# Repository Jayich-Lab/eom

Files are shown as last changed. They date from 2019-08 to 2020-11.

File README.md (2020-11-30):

# Electro-optic Modulator

The design for this project is based heavily on work done in the [Will Lab](https://www.will-lab.com/) that they generously shared with us.

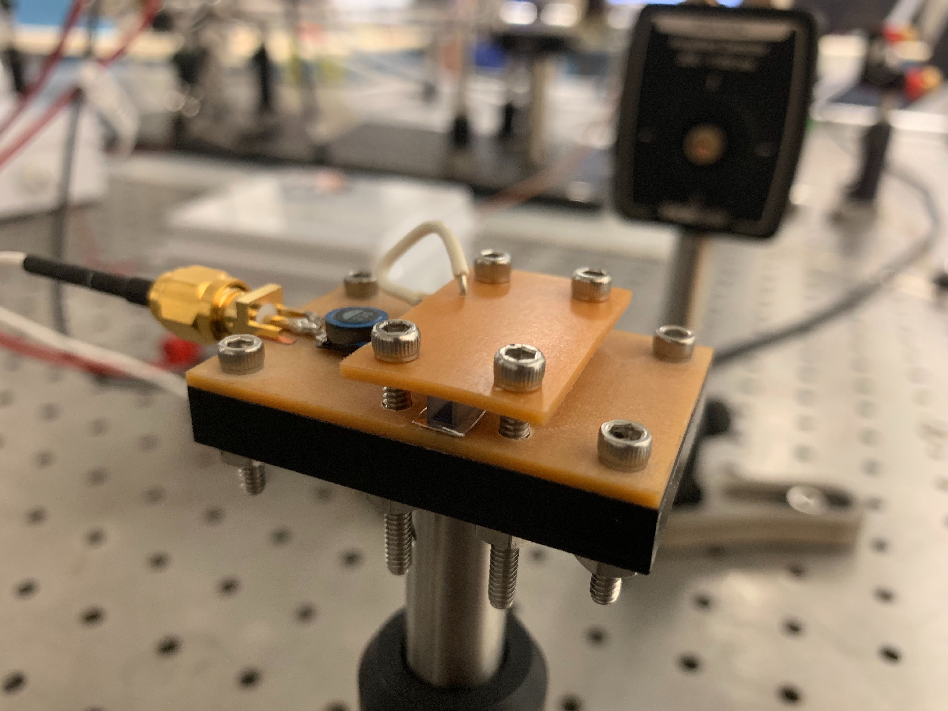
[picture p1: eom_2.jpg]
eom2


## EO Crystal 

We chose Lithium niobate (LiNbO<sub>3</sub>). It has a good Pockels effect, so we can minimize the input voltage to achieve the required modulation depth.
#### Relationship between the index of refraction, the electro-optic tensor, and the electric field:

<div align="center">\begin{pmatrix} \Delta(\frac{1}{n^{2}})_{1}\\ \Delta(\frac{1}{n^{2}})_{2}\\ \Delta(\frac{1}{n^{2}})_{3}\\ \Delta(\frac{1}{n^{2}})_{4}\\ \Delta(\frac{1}{n^{2}})_{5}\\ \Delta(\frac{1}{n^{2}})_{6} \end{pmatrix}= \begin{pmatrix} r_{11} &r_{12} &r_{13} \\ r_{21} &r_{22} &r_{23} \\ r_{31} &r_{32} &r_{33}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</div>

#### Electro-optic tensor of LiNbO<sub>3</sub> -- 3m(C3v) point group:
<div align="center">\bar{\bar{r}}=\begin{pmatrix} 0&-r_{22} &r_{13} \\ 0&r_{22} &r_{13} \\ 0&0 &r_{33} \\ 0&r_{42} &0 \\ r_{42}&0 &0 \\ -r_{22}&0 &0 \end{pmatrix} </div>  

#### Electro-optic Coefficient for Lithium Niobate (LiNbO<sub>3</sub>):

Electro-optic Coefficient | Value (pm/V) | 
:---: | :---: | 
r<sub>13</sub> | 9.6 
r<sub>22</sub> | 6.8
r<sub>33</sub> | 30.9 
r<sub>42</sub> | 32.6  

Taken from Boyd, 2003. This is within a [margin of error](http://www.lambdaphoto.co.uk/pdfs/Inrad_datasheet_LNB.pdf).

## Required voltage for changing a π phase

The "cut" of a crystal is the direction light is meant to propogate through it, e.g. Y-Cut means light will travel in the Y direction of crystal (where the X, Y, Z directions are specified by the crystal geometry). The voltage required for a pi phase shift is determined by the cut.

Applied electric field in Z direction, wave propagates in Y direction (Y-Cut):

<div align="center">V_{\pi}=\frac{d\lambda}{L(r_{33}n_{e}^{3}-r_{13}n_{o}^{3})}</div>  

<br/><br/>

Applied electric field in Y direction, wave propagates in Z direction (Z-Cut):
<div align="center">V_{\pi }=\frac{d\lambda }{4Ln_{0}^{3}r_{22}}</div>

#### Refractive Index for Lithium Niobate (LiNbO<sub>3</sub>) at different wavelengths

Value for n<sub>e</sub> | Value for n<sub>o</sub>  | Laser wavelength 
:---: | :---: | :---:
2.2666 | 2.3650 | 468nm
2.2342 | 2.3232 | 532nm
2.1875 | 2.2715 | 708nm
2.1845 | 2.2680 | 728nm
2.1702 | 2.2491 | 852nm
2.156 | 2.232 | 1064nm

---

## Final Design

We used Y-cut lithium niobate as our EO crystal. The bandwidth needed was 400nm-1100nm. We used different AR coatings to cover this range, one from 400-700nm and one from 700-1100nm. The crystal is 3mm x 3mm x 30mm, where one face is 3mm x 3mm.

#### The voltage needed across the EO crystal is:

λ( in meter ) | V<sub>π</sub> ( in volts )
:---: | :---: 
468 × 10<sup>-9</sup> | 201 V
532 × 10<sup>-9</sup> | 237 V
708 × 10<sup>-9</sup> | 335.65 V
852 × 10<sup>-9</sup> | 412 V
1064 × 10<sup>-9</sup> | 524.325 V

---

## Resonant circuit
We used a resonant circuit to minimize the input voltage which keeps the device safe to operate and avoids the extra effort of generating that high voltage.

The resonant frequency can be calculated:



We can use the usual parallel plate capacitor formula to calculate capacitance: 
<div align="center">C=\epsilon _{33}\frac{A}{d}</div>

Permittivity for Lithium Niobate is a tensor:
<div align="center">\begin{pmatrix} \epsilon_{11} &0 & 0 \\ 0 &\epsilon_{11} &0 \\ 0 &0 &\epsilon_{33} \end{pmatrix}</div>

If we apply electric field in Z direction, we are going to use ε<sub>33</sub>

Parameter | Value | Description
:---: | :---: | :---: 
ε<sub>33</sub> | 0.2543 × 10<sup>-9</sup> | permittivity for lithium niobate (in F⋅m<sup>−1</sup>) (about 28~30 times larger than ε<sub>0</sub>)
A | 0.003 × 0.03 | area of two plates (in meters<sup>2</sup>)
d | 0.003 | distance between plates (in meters)
C | 7.629 × 10<sup>-12</sup> | Capacitance of the crystal 

We use impedance to calculate the V<sub>eom</sub> with respect to input voltage (V<sub>eom</sub> is the voltage difference of two plates between the EO crystal). V<sub>input</sub> is the applied voltage before the resonant circuit. R<sub>sma</sub> is the resistance of SMA RF connector. R<sub>load</sub> is the resistance for the circuit.

<div align="center">V_{eom}=\frac{X_{C}}{X_{C}+X_{L}+R_{sma}+R_{load}}V_{input}</div>

<div align="center">\left |V _{eom} \right |=\frac{1}{\omega _{0}(R_{sma}+R_{load})C_{eom}}V_{input}</div>

R<sub>sma</sub> = R<sub>load</sub> = 50 Ω  

C = 7.629 × 10<sup>-12</sup> (approximately)

We need a modulation frequency f = 10 MHz = 10<sup>7</sup> Hz so we need L ~ 33.2uH

Quality factor for this circuit (RLC circuit) Q ~ 20

So the the maximum voltage required to operate is ~25 V.

There will obviously be stray capacitance and other non-ideal effects. In practice our quality factor was about 6, and our resonant frequency was ~8.7MHz.

---

Parts used:

- [ ] [33.2uH inductor chip](https://www.digikey.com/product-detail/en/tdk-corporation/SLF7032T-330MR75-2PF/445-2005-1-ND/755412)
- [ ] [RF Connector (50ohm)](https://www.digikey.com/products/en?keywords=SMA-J-P-H-ST-EM1)
- [ ] (2) Indium foil (~4mm x 30mm)
- [ ] Lithium Niobate crystal
- [ ] [Delrin stock (to be milled, <13mm thickness is ideal)](https://www.mcmaster.com/plastics/wear-resistant-easy-to-machine-delrin-acetal-resin-sheets-bars-and-strips/thickness~1-2/)
- [ ] (8) 4-40 screws
- [ ] (8) 4-40 nuts
- [ ] (1) 8/32 screw
- [ ] [(4) Spring Washers](https://www.mcmaster.com/spring-washers/curved-disc-springs-6/id~0-135/)
- [ ] 8/32 compatible 1/2" optics post
- [ ] 1/2" optics post holder

---

# Instructions on how to build the EOM

First, mill the mount (generally any plastic works, but delrin was used for our EOMs). The mount design is in the repo as a fusion360 model and an stl/step model. 

Second, mill the top and bottom pcbs. Set a large clearance (20 mm) when milling them such that all copper visible on the board is for required lines. The eo crystal will be sandwiched in between the top and bottom pcbs, with the indium foil as a cushion. You should then solder the inductor and the sma connector onto the bottom pcb. It is advisable to solder the top pcb to the bottom for the ground connection at this point (leaving a reasonable amount of slack on the wire used).

You then want to take the eo crystal and gently place that between ~4mmx30mm strips of indium foil between the pcbs. (Make sure the side of the eo crystal used is correct!) Finally, screw everything together -- first screw the mount onto the 1/2" post, then the bottom pcb onto the mount, then the top pcb onto the mount (through the bottom pcb). Note that we use 4-40 screws with spring washers to do so.

You should be careful not to break the eo crystal when tightening. We found that not much force is required to make electrical contact. Note that our resonant frequency on the circuit was 8.7MHz, but you could change this by changing the inductance (were you in need of a different modulation frequency).

N.B. Try to make sure the screws are tightened somewhat evenly. Uneven pressures on the crystal are most likely to break it (fixed by spring washers).

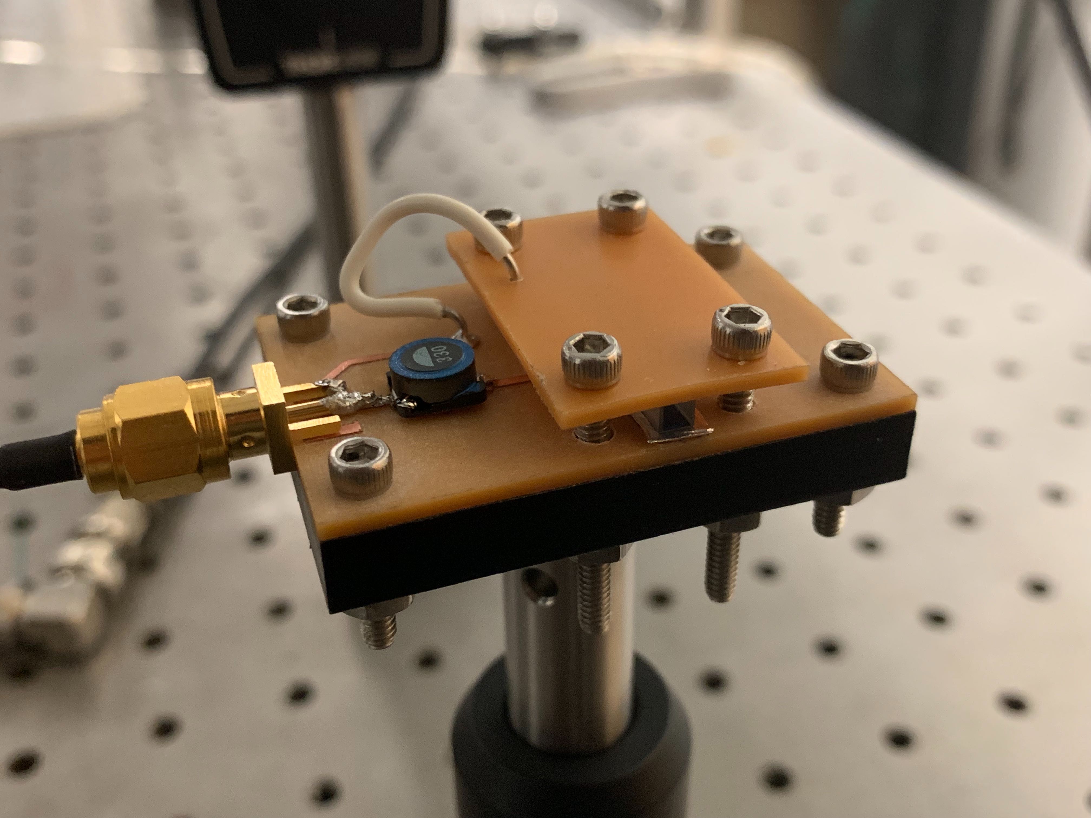
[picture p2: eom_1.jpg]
eom1


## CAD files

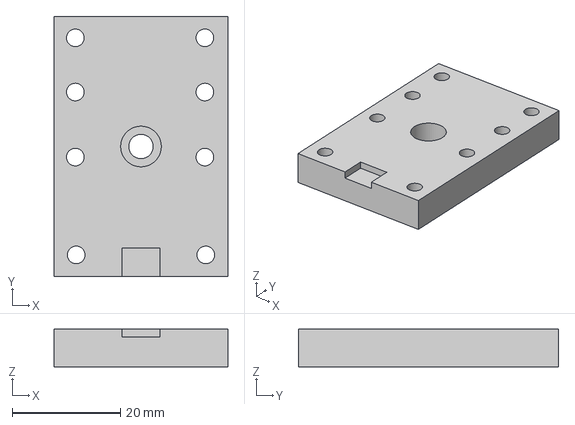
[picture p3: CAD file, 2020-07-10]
design/plastic mount/EOM_pcb_adapter v6.step
32.1 x 48.0 x 7.00 mm

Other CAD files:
design/plastic mount/EOM_pcb_adapter v6.f3d
design/plastic mount/EOM_pcb_adapter v6.stl

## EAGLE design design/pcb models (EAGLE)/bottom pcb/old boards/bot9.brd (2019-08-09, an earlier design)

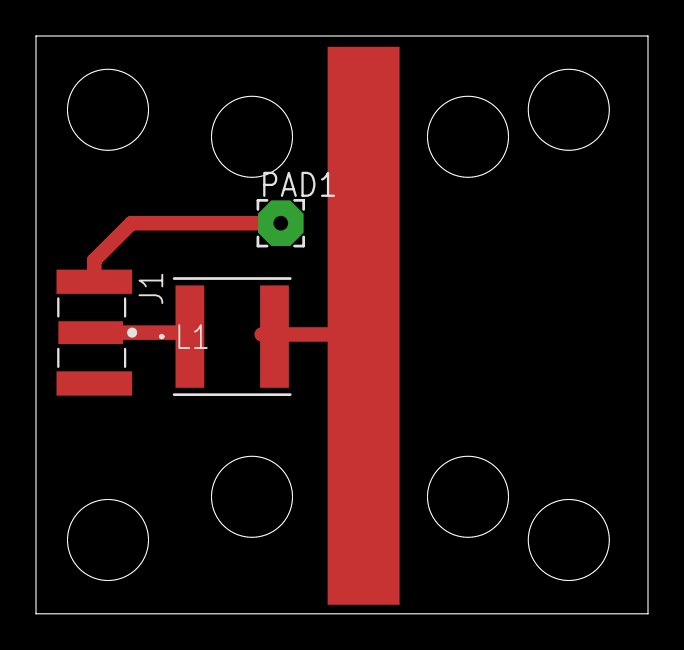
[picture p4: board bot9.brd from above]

Board: 2 copper layers, 34.0 x 32.1 mm, 3 parts (0 on the bottom side), 2 nets.

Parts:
J1: SMA-J-P-H-ST-EM1
L1: NR6028T330M; IND_TAIYO_NR6028
PAD1: 2,54/0,8

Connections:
unnamed: J1.1, L1.2
unnamed: J1.2_1, J1.2_2, J1.3_1, J1.3_2, PAD1.1

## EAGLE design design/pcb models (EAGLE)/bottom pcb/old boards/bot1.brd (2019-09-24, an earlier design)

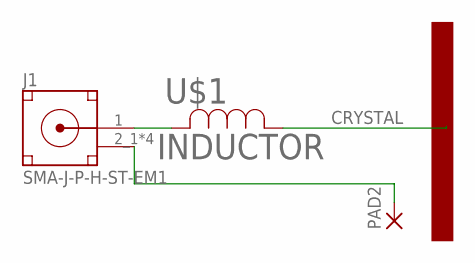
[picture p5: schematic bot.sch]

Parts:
J1: SMA-J-P-H-ST-EM1
PAD2: 2,54/1,1
U$1: INDUCTOR; IND_7030

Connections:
2L: J1.1 (SIGNAL), U$1.2
CRYSTAL: U$1.1
GND: J1.2_1 (GND), J1.2_2 (GND), J1.3_1 (GND), J1.3_2 (GND), PAD2.1

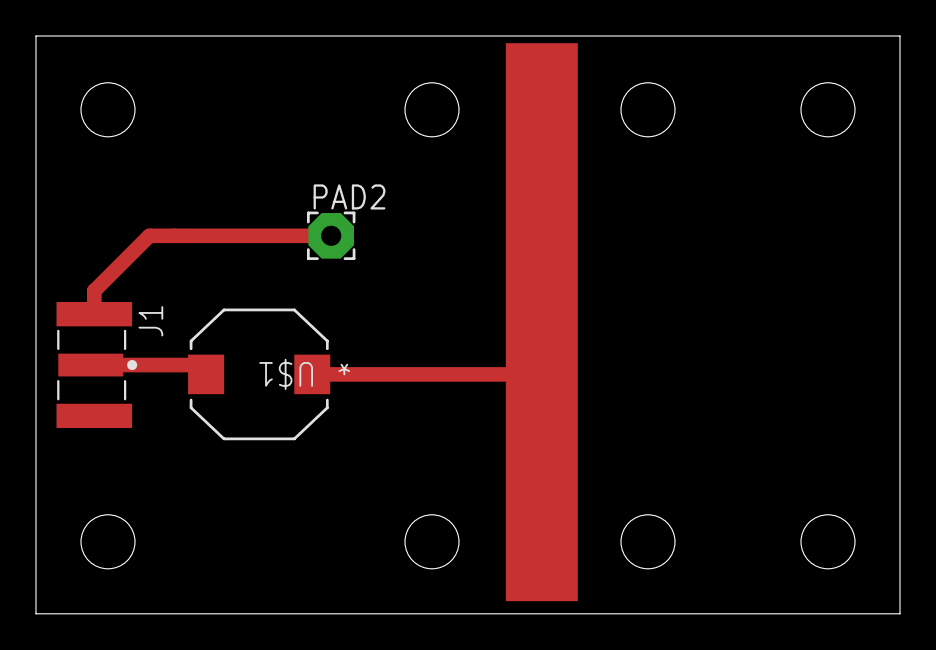
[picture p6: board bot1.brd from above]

Board: 2 copper layers, 48.0 x 32.1 mm, 3 parts (0 on the bottom side), 2 nets.

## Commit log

2019-02-21 add material for eom
    [top.brd, top.sch]
2019-02-21 add root for pcb
    [bot.brd, bot.sch, top.brd, top.sch]
2019-04-03 top pcb board
    [bot.sch, top.brd]
2019-07-10 pcb_bottom finished
    [bot.brd, bot.sch]
2019-07-11 add top board
    [top.brd, top.sch]
2019-08-28 reorg
    reorg
    [bot.brd, bot.sch, eom.brd, eom.sch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]
2020-07-09 update mount files
    [EOM_pcb_adapter v5.f3d, mount.stl]
2020-07-10 8/32 head diameter
    [EOM_pcb_adapter v5.f3d, EOM_pcb_adapter v6.f3d, EOM_pcb_adapter v6.step, EOM_pcb_adapter v6.stl]
2020-09-03 voltage clarification
2021-08-05 eom pcb
    [bot1.brd, bot9.brd]
